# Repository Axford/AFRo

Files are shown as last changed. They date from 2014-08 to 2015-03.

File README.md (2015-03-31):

# AFRo

Assisted Feeding Robot

In development for REMAP UK

Design notes (WIP):
https://docs.google.com/document/d/1HDJsVby1FxGu6IQ2XBOvq7dboFC9hibPxshcKR86C0M/pub

## Hardware

OpenSCAD model, assembly guide and STL for printed parts

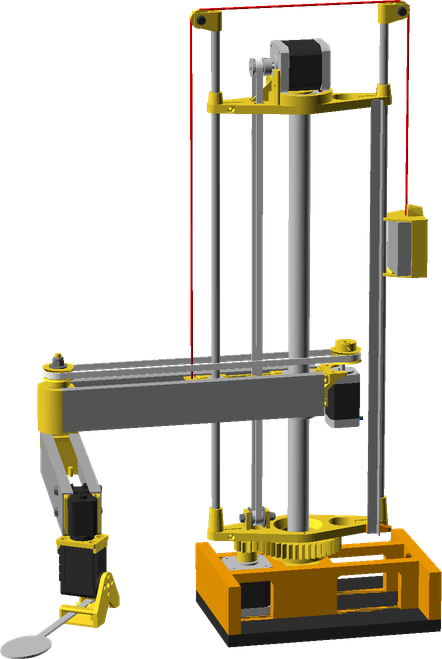
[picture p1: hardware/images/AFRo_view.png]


## Software

**AFRoHost**
Host interface for controlling/debugging the arm, written in Processing.  

Requires the following libraries:
 - gwoptics, from http://www.gwoptics.org/processing/gwoptics_p5lib/
 - controlP5, from http://www.sojamo.de/libraries/controlP5

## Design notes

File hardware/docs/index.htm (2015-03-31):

# AFRo Documentation

## Assembly Guide

- AFRo

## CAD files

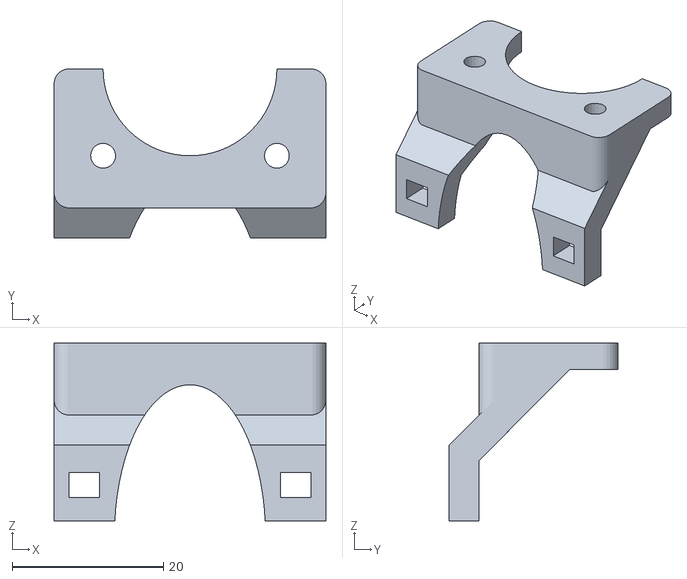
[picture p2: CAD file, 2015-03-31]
hardware/printedparts/stl/ElbowMotorPlate.stl
36.0 x 22.4 x 23.5

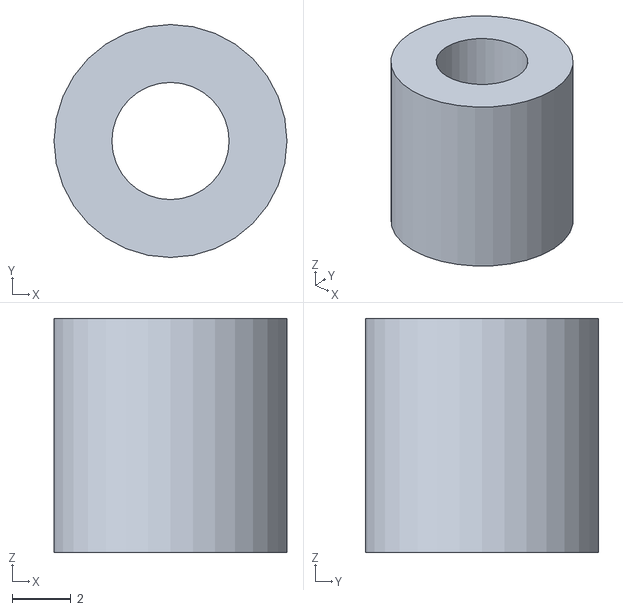
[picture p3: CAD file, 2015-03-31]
hardware/sandbox/stl/elbow bearing adapter.stl
7.95 x 7.95 x 8.00

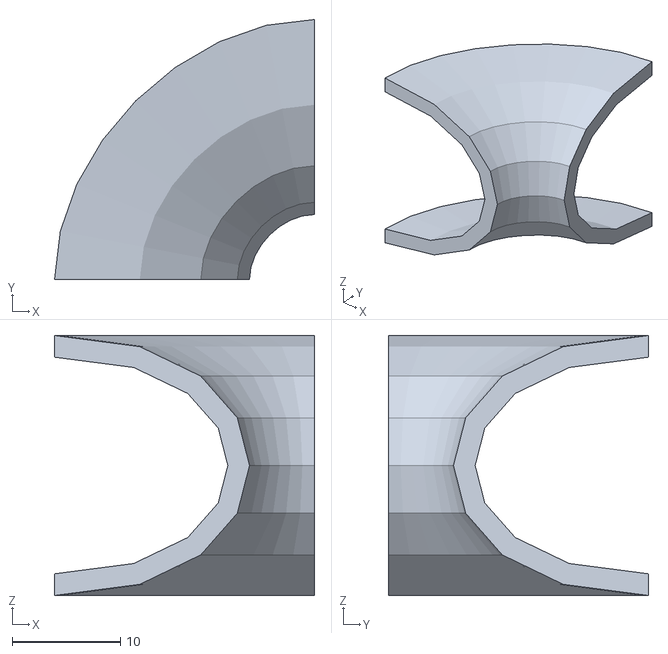
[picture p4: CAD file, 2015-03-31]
hardware/utils/surfacesolids/curve_section.stl
24.0 x 24.0 x 24.0

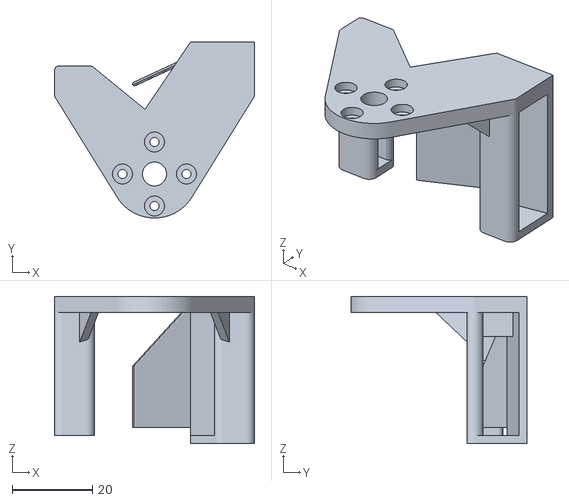
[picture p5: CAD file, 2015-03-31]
hardware/printedparts/stl/SpoonHolder.stl
50.0 x 44.0 x 36.8

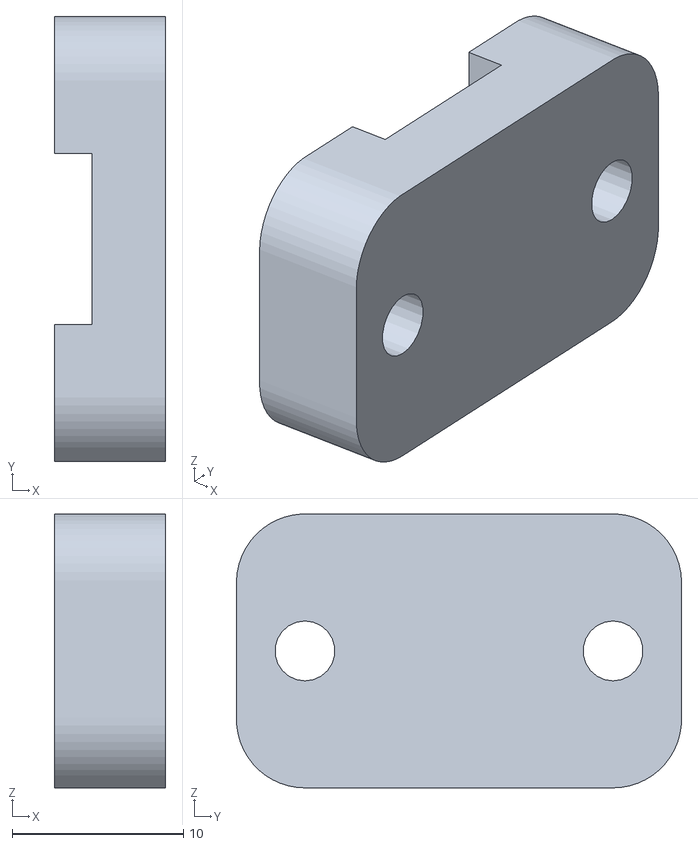
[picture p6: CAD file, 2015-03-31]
hardware/printedparts/stl/ShoulderBeltClamp.stl
6.50 x 26.0 x 16.0

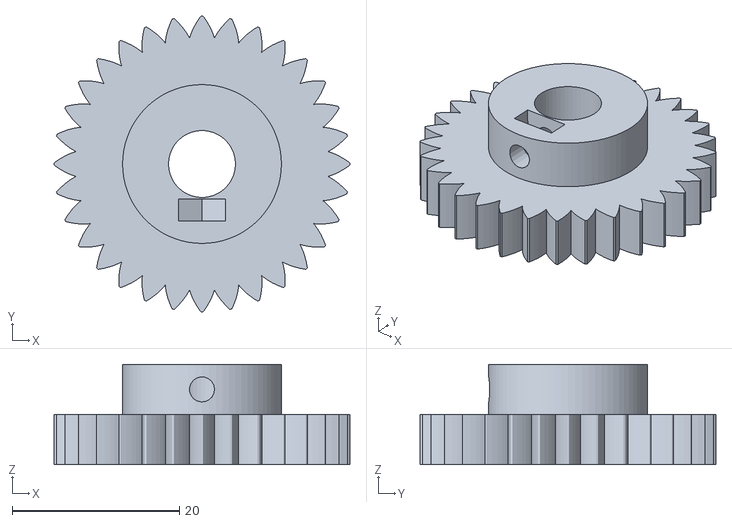
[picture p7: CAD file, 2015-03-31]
hardware/printedparts/stl/ElbowDrivenGear.stl
35.4 x 35.4 x 12.0

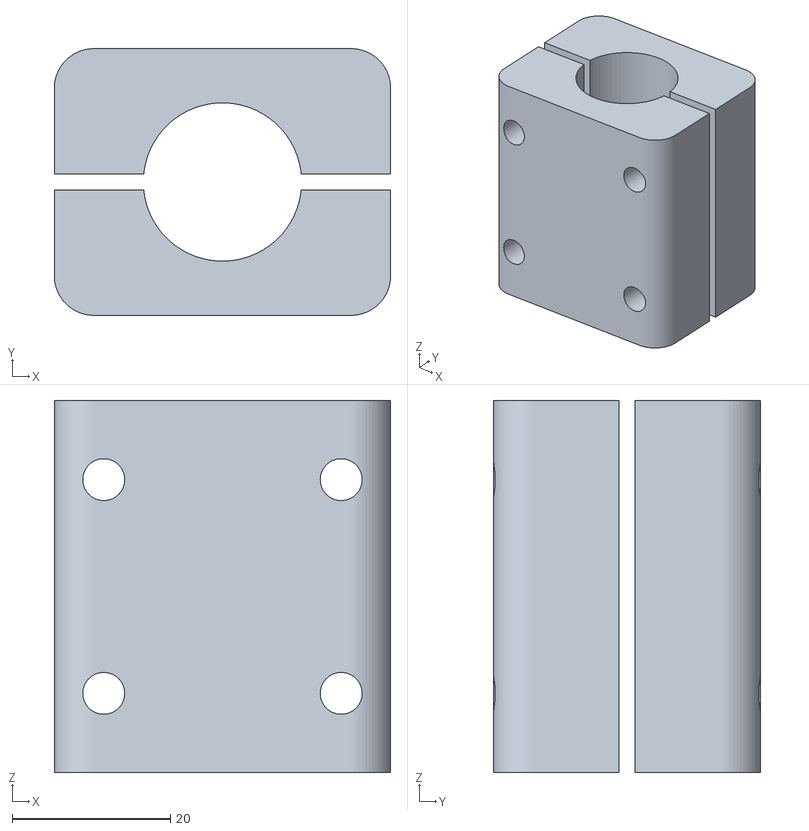
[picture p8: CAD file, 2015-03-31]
hardware/printedparts/stl/BaseBracket.stl
42.5 x 33.7 x 47.0

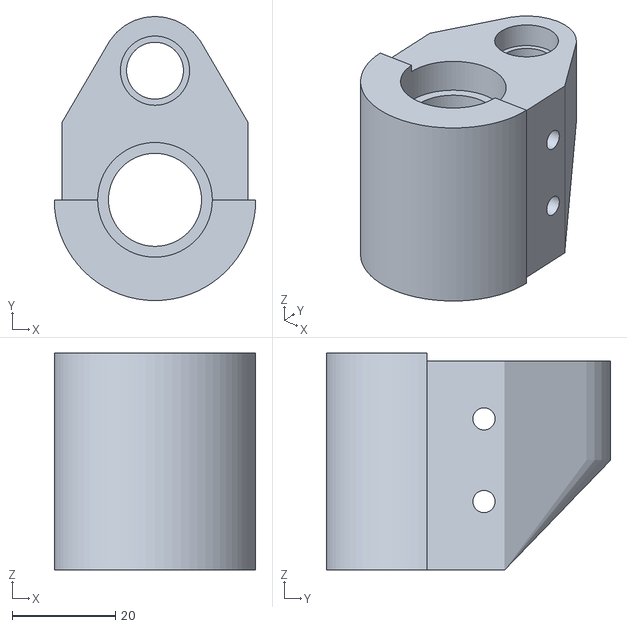
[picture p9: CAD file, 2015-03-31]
hardware/printedparts/stl/ElbowJoint.stl
39.0 x 55.0 x 42.0

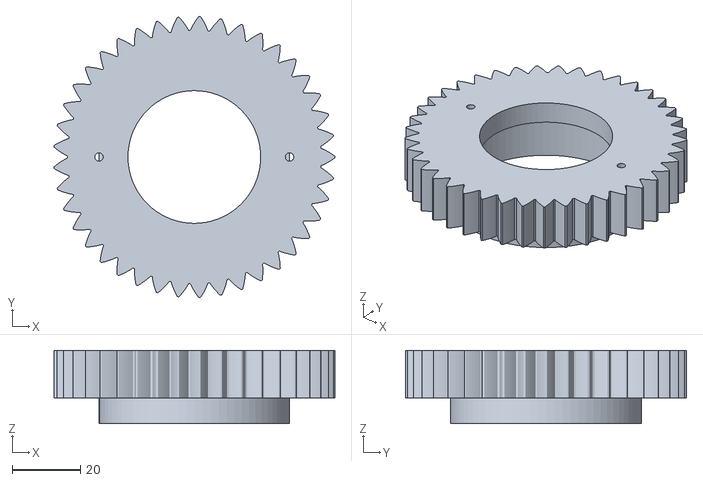
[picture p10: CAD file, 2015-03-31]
hardware/printedparts/stl/TorsoBigGear.stl
82.6 x 82.6 x 21.5

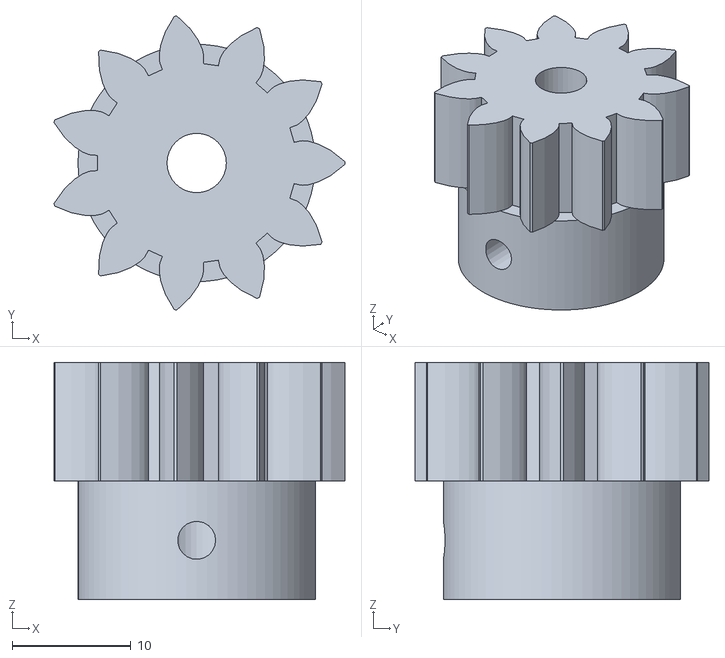
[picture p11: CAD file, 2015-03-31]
hardware/printedparts/stl/TorsoDriveGear.stl
24.5 x 24.8 x 20.0

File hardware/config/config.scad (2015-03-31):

//
// PMount
//
// Configuration file
//
bom = 0;                        // 0 no bom, 1 assemblies and stls, 2 vitamins as well
exploded = 0;                   // 1 for exploded view
simplify = false;    			// reduces complexity of some parts, e.g. alu extrusions

show_jigs = true;               // show printed jigs required to build the machine
show_support = true;            // show support structures, must be set when generating STLs

debugConnectors = false;  //  show "attach" points

// Real-world colors for various parts & vitamins
use_realistic_colors = true;    // true for "real" colors, false for "distinct" colors (useful during design and for build instructions)
printed_plastic_color = "orange";
cable_strip_real_color = "fuchsia";
belt_real_color = "yellow";
bulldog_real_color ="black";

eta = 0.01;                     // small fudge factor to stop CSG barfing on coincident faces.
$fa = 5;
$fs = 0.5;

perim = 0.5;    // perim extrusion width for 0.2 or 0.3 layer height
layers = 0.3;
2perim = 2*perim;
4perim = 4*perim;


// Debugging

DebugConnectors = 1;  			// set to 1 to debug, set to 0 for production
DebugCoordinateFrames = 1; 		// set to 1 to debug, set to 0 for production


// Visualisation

// set to true to use STL for printed parts rather than rendering on the fly
UseSTL = true;
STLPath = "../printedparts/stl/";
UseVitaminSTL = true;
VitaminSTL = "../vitamins/stl/";

$Explode  = false;
$ShowStep = 100;

$DefaultViewSize = [400, 300];


//
// Hole sizes
//
No2_pilot_radius = 1.7 / 2;       // self tapper into ABS
No4_pilot_radius = 2.0 / 2;       // wood screw into soft wood
No6_pilot_radius = 2.0 / 2;       // wood screw into soft wood

No2_clearance_radius = 2.5 / 2;
No4_clearance_radius = 3.5 / 2;
No6_clearance_radius = 4.0 / 2;

M2_tap_radius = 1.5 / 2;
M2_clearance_radius = 2.3 / 2;
M2_nut_radius = 4.6 / 2;
M2_nut_trap_depth = 2;

M2p5_tap_radius = 2.05 / 2;
M2p5_clearance_radius= 2.8 / 2;   // M2.5
M2p5_nut_trap_depth = 2.5;

M3_tap_radius = 2.5 / 2;
M3_clearance_radius = 3.3 / 2;
M3_nut_radius = 6.5 / 2;
M3_nut_trap_depth = 3;

M4_tap_radius = 3.3 / 2;
M4_clearance_radius = 2.2;
M4_nut_radius = 8.2 / 2;
M4_nut_trap_depth = 4;

M5_tap_radius = 4.2 / 2;
M5_clearance_radius = 5.3 / 2;
M5_nut_radius = 9.2 / 2;
M5_nut_depth = 4;

M6_tap_radius = 5 / 2;
M6_clearance_radius = 6.4 / 2;
M6_nut_radius = 11.6 / 2;
M6_nut_depth = 5;

M8_tap_radius = 6.75 / 2;
M8_clearance_radius = 8.4 / 2;
M8_nut_radius = 15.4 / 2;
M8_nut_depth = 6.5;

M10_tap_radius = 8 / 2;
M10_clearance_radius = 10.4 / 2;
M10_nut_radius = 19.6 / 2;
M10_nut_depth = 8;



include <colors.scad>
include <utils.scad>
include <vitamins.scad>
include <machine.scad>
include <cutparts.scad>
include <printedparts.scad>
include <assemblies.scad>

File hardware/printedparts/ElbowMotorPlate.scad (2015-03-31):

module ElbowMotorPlate_stl() {
	// origin at post, base of shoulder
	
	bh = linear_bearing_height(ShoulderRodBearing);
	bigod = linear_bearing_od(LM20UU);
	nw = NEMA_width(NEMA11);
	
	sw = ShoulderWidth;
	
	edgeOfBracket = bigod/2 + tw;
	
	d = ElbowMotorOffset;

	d1 = d - edgeOfBracket -  tw;
	
	printedPart("printedparts/ElbowMotorPlate.scad", "Elbow Motor Plate", "ElbowMotorPlate_stl()") {

        view(t=[-1, 2, 3]);

        if (UseSTL) {
            import(str(STLPath, "ElbowMotorPlate.stl"));
        } else {
            difference() {
                union() {

                    // motor plate
                    translate([-sw/2, edgeOfBracket + tw, bh -dw ])
                        roundedRect([sw, d1, dw + 1.5], tw/2);

                    // back rest
                    translate([-sw/2, edgeOfBracket + tw, dw ])
                        roundedRect([sw, tw, bh - dw], tw/2);

                    // mating plate
                    translate([-sw/2, edgeOfBracket + eta, 14 - dw ])
                        rotate([0, 90, 0])
                        trapezoidPrism(14 + tw/2, 14-tw, tw + tw/2, -tw - tw/2, sw);

                    // fillets
                    for (i=[0,1])
                        mirror([i,0,0])
                        translate([sw/2 - dw/2, edgeOfBracket + tw + tw/2, bh - dw])
                        rotate([0, 90, 0])
                        right_triangle(10, 10, dw, center = true);

                    // back rest fillet

                }

                // motor fixings / boss
                translate([0, ElbowMotorOffset, bh+1.5]) {
                    // boss
                    cylinder(r=NEMA_big_hole(NEMA11)+0.3, h=50, center=true);

                    // motor fixings
                    for(a = [0: 90 : 90 * (4 - 1)])
                        rotate([0, 0, a])
                        translate([NEMA_holes(NEMA11)[0], NEMA_holes(NEMA11)[1], 0])
                        cylinder(r=screw_clearance_radius(M3_cap_screw), h=50, center=true);
                }

                // shoulder bracket fixings
                for (i=[0,1])
                    mirror([i,0,0])
                    translate([ShoulderWidth/2 - tw, edgeOfBracket, bh - ShoulderHeight/2 + 2]) {
                        // bore
                        cube([4, 100, 3.3], center=true);

                    }

                // trim for screw heads
                translate([-sw/2-5, edgeOfBracket + tw, 12 - dw - eta ])
                    rotate([0, 90, 0])
                    trapezoidPrism(12 + tw/2, 12-tw, tw + tw/2, -tw - tw/2, sw+10);

                // weight loss
                translate([0,0, 0])
                    scale([0.5,1,1])
                    rotate([90,0, 0])
                    cylinder(r=20, h=100, center=true);

            }
        }
    }
}

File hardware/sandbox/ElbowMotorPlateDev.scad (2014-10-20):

include <../config/config.scad>


ShoulderBracketLeft_stl();
ShoulderBracketRight_stl();

ElbowMotorPlate_stl();

bh = linear_bearing_height(ShoulderRodBearing);

// motor frame
translate([0, ElbowMotorOffset, bh - dw])
	frame();


translate([-80, 0, 0]) ShoulderAssembly();

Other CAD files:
hardware/sandbox/printedpart_ElbowMotorPlate.scad
assemblies/LowerArm.scad
assemblies/UpperArm.scad
hardware/AFRo.scad
hardware/assemblies/AFRo.scad
hardware/assemblies/CableGuide.scad
hardware/assemblies/Hand.scad
hardware/assemblies/LowerArm.scad
hardware/assemblies/Shoulder.scad
hardware/assemblies/Torso.scad
hardware/assemblies/mk1/AFRo.scad
hardware/assemblies/mk1/Hand.scad
hardware/assemblies/mk1/LowerArm.scad
hardware/assemblies/mk1/MotorCoupling.scad
hardware/assemblies/mk1/Shoulder.scad
hardware/assemblies/mk1/UpperArm.scad
hardware/config/assemblies.scad
hardware/config/colors.scad
hardware/config/cutparts.scad
hardware/config/machine.scad
hardware/config/machine_mk1.scad
hardware/config/printedparts.scad
hardware/config/utils.scad
hardware/config/vitamins.scad
hardware/cutparts/LowerArmLeftSide.scad
hardware/design/scara concept 1.skp
hardware/design/scara concept 1~.skp
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

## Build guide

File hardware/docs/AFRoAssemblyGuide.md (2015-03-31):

# AFRo
# Assembly Guide

## Bill of Materials

Make sure you have all of the following parts before you begin.

### Vitamins

Qty | Vitamin | Image
--- | --- | ---
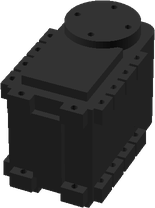
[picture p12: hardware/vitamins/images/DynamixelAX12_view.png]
2 | [Dynamixel AX12]() |  | 
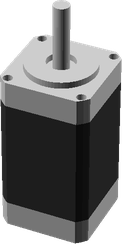
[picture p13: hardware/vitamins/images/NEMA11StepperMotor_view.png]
1 | [NEMA11 Stepper Motor]() |  | 
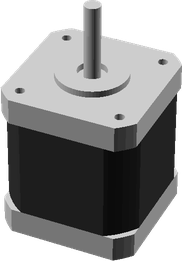
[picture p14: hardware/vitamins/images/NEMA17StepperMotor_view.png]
2 | [NEMA17 Stepper Motor]() |  | 
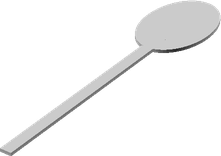
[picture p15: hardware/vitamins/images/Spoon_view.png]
1 | [Spoon]() |  | 
1 | [Threaded Rod M6 x 105mm]() |  | 
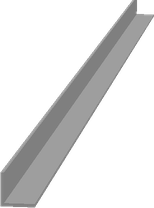
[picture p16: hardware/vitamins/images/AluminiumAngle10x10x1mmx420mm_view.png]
1 | [Aluminium Angle 10x10x1mm x 420mm]() |  | 
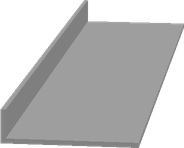
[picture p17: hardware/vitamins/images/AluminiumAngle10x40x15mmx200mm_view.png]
4 | [Aluminium Angle 10x40x1.5mm x 200mm]() |  | 
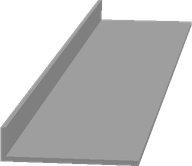
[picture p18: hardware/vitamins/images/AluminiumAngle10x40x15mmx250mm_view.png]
2 | [Aluminium Angle 10x40x1.5mm x 250mm]() |  | 
1 | [Aluminium Tube 8mm OD 6mm ID x 79mm]() |  | 
2 | [Ball Bearing 608]() |  | 
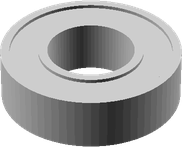
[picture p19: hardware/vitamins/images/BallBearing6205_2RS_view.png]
2 | [Ball Bearing 6205_2RS]() |  | 
6 | [Ball Bearing 624]() |  | 
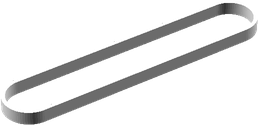
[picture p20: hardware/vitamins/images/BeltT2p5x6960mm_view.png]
1 | [Belt T2p5x6 960mm]() |  | 
1 | [Belt T2p5x6 610mm]() |  | 
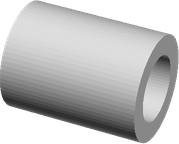
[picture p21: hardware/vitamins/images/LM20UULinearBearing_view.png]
1 | [LM20UU Linear Bearing]() |  | 
1 | [LM8UU Linear Bearing]() |  | 
1 | [T2.5x18 Pulley]() |  | 
4 | [M2 Nut]() |  | 
6 | [Nyloc M4 Nut]() |  | 
1 | [M6 Nut]() |  | 
1 | [Nyloc M6 Nut]() |  | 
12 | [M2 pan screw x 6mm]() |  | 
2 | [M4 cap screw x 20mm]() |  | 
1 | [M4 cap screw x 50mm]() |  | 
1 | [M4 hex screw x 30mm]() |  | 
2 | [M4 hex screw x 40mm]() |  | 
19 | [M4 Washer 9x0.8]() |  | 
2 | [M5 Washer 20x1.4]() |  | 
4 | [M6 Washer 12x1.5]() |  | 
1 | [M8 Washer 17x1.8]() |  | 

### Cut Parts

Qty | Part Name | Image
--- | --- | ---
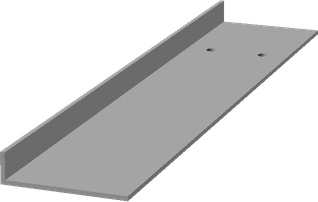
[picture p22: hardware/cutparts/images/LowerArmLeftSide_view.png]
2 | Lower Arm Left Side |  | 

### Printed Parts

Qty | Part Name | Image
--- | --- | ---
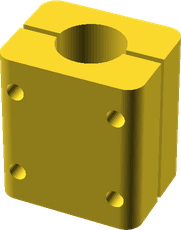
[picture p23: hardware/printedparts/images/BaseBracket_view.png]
1 | [Base Bracket](../printedparts/stl/BaseBracket.stl) |  | 
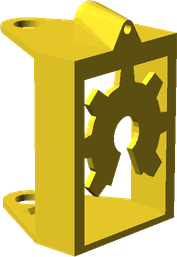
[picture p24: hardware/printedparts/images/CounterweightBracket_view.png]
1 | [Counterweight Bracket](../printedparts/stl/CounterweightBracket.stl) |  | 
2 | [Counterweight Idler Guide](../printedparts/stl/CounterweightIdlerGuide.stl) |  | 
2 | [Counterweight Idler](../printedparts/stl/CounterweightIdler.stl) |  | 
1 | [Counterweight Line Bracket](../printedparts/stl/CounterweightLineBracket.stl) |  | 
1 | [Elbow Drive Pulley](../printedparts/stl/ElbowDrivePulley.stl) |  | 
1 | [Elbow Driven Gear](../printedparts/stl/ElbowDrivenGear.stl) |  | 
1 | [Elbow Driven Pulley](../printedparts/stl/ElbowDrivenPulley.stl) |  | 
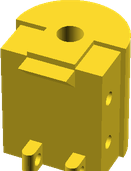
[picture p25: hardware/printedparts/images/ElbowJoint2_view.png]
1 | [Elbow Joint 2](../printedparts/stl/ElbowJoint2.stl) |  | 
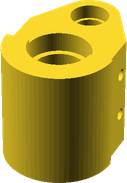
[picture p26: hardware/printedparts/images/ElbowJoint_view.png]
1 | [Elbow Joint](../printedparts/stl/ElbowJoint.stl) |  | 
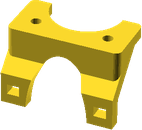
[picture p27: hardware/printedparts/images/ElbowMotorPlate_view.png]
1 | [Elbow Motor Plate](../printedparts/stl/ElbowMotorPlate.stl) |  | 
2 | [Lower Arm Servo Bracket](../printedparts/stl/LowerArmServoBracket.stl) |  | 
1 | [Shoulder Belt Clamp](../printedparts/stl/ShoulderBeltClamp.stl) |  | 
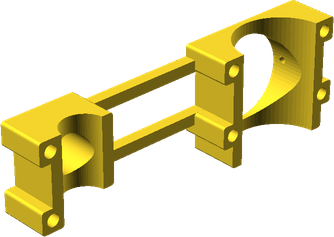
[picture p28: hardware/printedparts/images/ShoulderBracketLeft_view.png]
1 | [Shoulder Bracket Left](../printedparts/stl/ShoulderBracketLeft.stl) |  | 
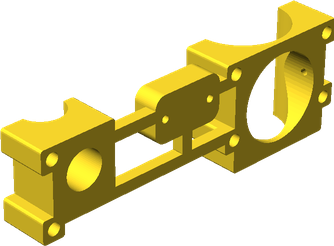
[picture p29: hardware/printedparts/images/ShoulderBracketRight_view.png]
1 | [Shoulder Bracket Right](../printedparts/stl/ShoulderBracketRight.stl) |  | 
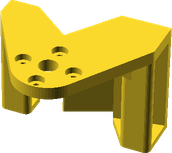
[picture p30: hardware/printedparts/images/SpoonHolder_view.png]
1 | [Spoon Holder](../printedparts/stl/SpoonHolder.stl) |  | 
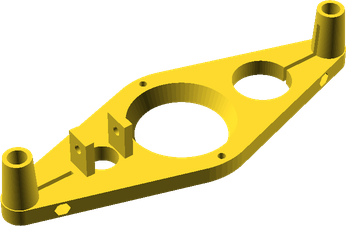
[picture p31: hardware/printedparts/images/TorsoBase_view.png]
1 | [Torso Base](../printedparts/stl/TorsoBase.stl) |  | 
1 | [Torso Bearing Collar](../printedparts/stl/TorsoBearingCollar.stl) |  | 
1 | [Torso Bearing Top Collar](../printedparts/stl/TorsoBearingTopCollar.stl) |  | 
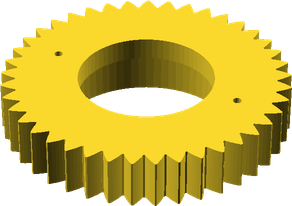
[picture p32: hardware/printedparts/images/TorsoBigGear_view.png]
1 | [Torso Big Gear](../printedparts/stl/TorsoBigGear.stl) |  | 
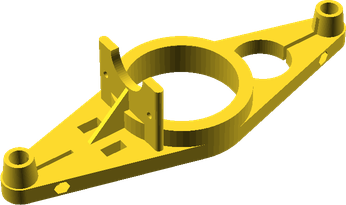
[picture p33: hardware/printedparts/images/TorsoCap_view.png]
1 | [Torso Cap](../printedparts/stl/TorsoCap.stl) |  | 
1 | [Torso Drive Gear](../printedparts/stl/TorsoDriveGear.stl) |  | 
1 | [Wrist Bracket](../printedparts/stl/WristBracket.stl) |  | 

# Cutting Instructions

## Lower Arm Left Side (x2)

### Vitamins

Qty | Vitamin | Image
--- | --- | ---
4 | [Aluminium Angle 10x40x1.5mm x 200mm]() |  | 

### Fabrication Steps

1. Cut aluminium angle to 200mm
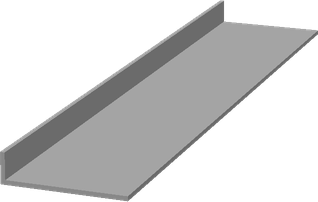
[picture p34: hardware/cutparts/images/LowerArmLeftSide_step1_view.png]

2. Drill 4mm diameter fixing holes


# Assembly Instructions

## Spoon

### Vitamins

Qty | Vitamin | Image
--- | --- | ---
1 | [Dynamixel AX12]() |  | 
1 | [Spoon]() |  | 
4 | [M2 Nut]() |  | 
4 | [M2 pan screw x 6mm]() |  | 

### Printed Parts

Qty | Part Name | Image
--- | --- | ---
1 | [Spoon Holder](../printedparts/stl/SpoonHolder.stl) |  | 

### Assembly Steps

1. Push M2 nuts into the back of the servo fixing tabs
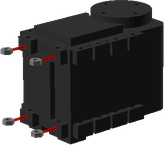
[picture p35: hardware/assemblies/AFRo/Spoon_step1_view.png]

2. Attach the spoon holder to the servo
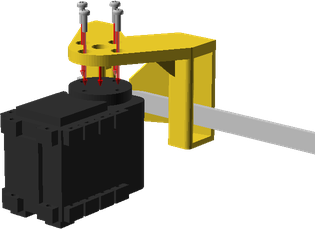
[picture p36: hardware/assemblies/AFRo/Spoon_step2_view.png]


## Hand

### Vitamins

Qty | Vitamin | Image
--- | --- | ---
1 | [Dynamixel AX12]() |  | 
8 | [M2 pan screw x 6mm]() |  | 

### Printed Parts

Qty | Part Name | Image
--- | --- | ---
1 | [Wrist Bracket](../printedparts/stl/WristBracket.stl) |  | 

### Sub-Assemblies

Qty | Name 
--- | --- 
1 | Spoon

### Assembly Steps

1. Screw the wrist bracket onto the wrist servo
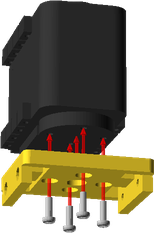
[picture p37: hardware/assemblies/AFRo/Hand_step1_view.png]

2. Push the spoon assembly into the wrist bracket
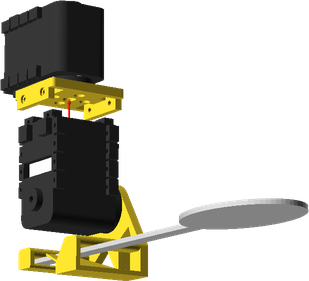
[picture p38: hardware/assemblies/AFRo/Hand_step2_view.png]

3. Screw through the bracket into the servo fixings
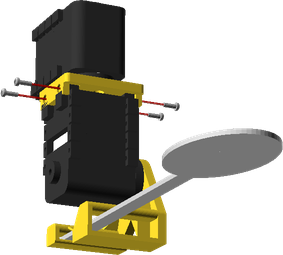
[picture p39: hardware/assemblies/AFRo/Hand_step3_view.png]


## Lower Arm

### Vitamins

Qty | Vitamin | Image
--- | --- | ---
2 | [Nyloc M4 Nut]() |  | 
2 | [M4 hex screw x 40mm]() |  | 
4 | [M4 Washer 9x0.8]() |  | 

### Printed Parts

Qty | Part Name | Image
--- | --- | ---
1 | [Elbow Joint 2](../printedparts/stl/ElbowJoint2.stl) |  | 
2 | [Lower Arm Servo Bracket](../printedparts/stl/LowerArmServoBracket.stl) |  | 

### Sub-Assemblies

Qty | Name 
--- | --- 
1 | Hand

### Assembly Steps

1. Push the servo brackets onto the servo, optionally screw them into place
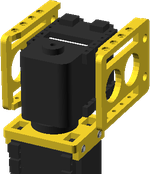
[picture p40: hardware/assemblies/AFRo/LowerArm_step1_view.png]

2. Bolt through the aluminium channels and servo brackets
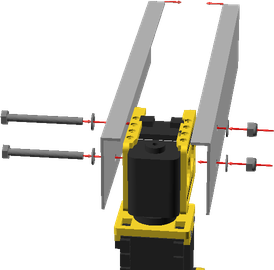
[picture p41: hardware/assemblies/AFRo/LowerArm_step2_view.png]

3. Bolt through the aluminium channels and elbow joint
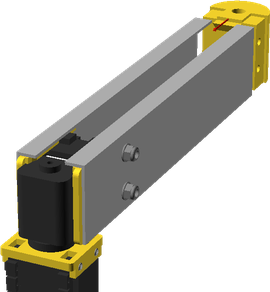
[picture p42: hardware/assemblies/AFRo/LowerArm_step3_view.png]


## Elbow Joint

### Vitamins

Qty | Vitamin | Image
--- | --- | ---
1 | [Threaded Rod M6 x 105mm]() |  | 
1 | [Aluminium Tube 8mm OD 6mm ID x 79mm]() |  | 
2 | [Ball Bearing 608]() |  | 
2 | [Ball Bearing 624]() |  | 
1 | [Belt T2p5x6 610mm]() |  | 
1 | [Nyloc M4 Nut]() |  | 
1 | [M6 Nut]() |  | 
1 | [Nyloc M6 Nut]() |  | 
1 | [M4 cap screw x 50mm]() |  | 
3 | [M4 Washer 9x0.8]() |  | 
4 | [M6 Washer 12x1.5]() |  | 
1 | [M8 Washer 17x1.8]() |  | 

### Printed Parts

Qty | Part Name | Image
--- | --- | ---
1 | [Elbow Driven Gear](../printedparts/stl/ElbowDrivenGear.stl) |  | 
1 | [Elbow Driven Pulley](../printedparts/stl/ElbowDrivenPulley.stl) |  | 
1 | [Elbow Joint](../printedparts/stl/ElbowJoint.stl) |  | 

### Sub-Assemblies

Qty | Name 
--- | --- 
1 | Lower Arm

### Assembly Steps

1. Loosely assemble the driven gear set and push fit into the elbow joint
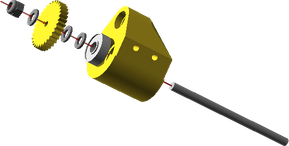
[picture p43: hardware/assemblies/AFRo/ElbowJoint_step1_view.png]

2. Assemble the pulley set
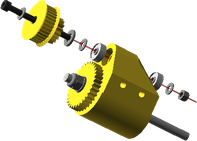
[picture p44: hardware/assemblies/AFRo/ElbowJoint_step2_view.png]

3. Slide the aluminium tube over the threaded rod and push fit the lower bearing
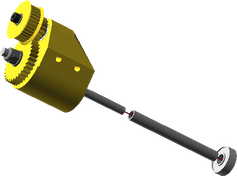
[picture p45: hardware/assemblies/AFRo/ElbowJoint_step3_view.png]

4. Connect the lower arm
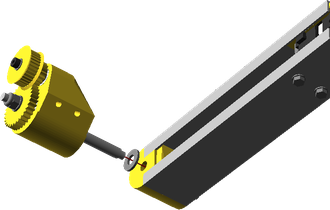
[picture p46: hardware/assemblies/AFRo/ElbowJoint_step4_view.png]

5. Slip the belt round the pulley - this be connected later
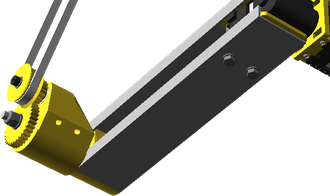
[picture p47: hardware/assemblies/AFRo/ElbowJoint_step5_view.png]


## Counterweight Idler (x2)

### Vitamins

Qty | Vitamin | Image
--- | --- | ---
2 | [Ball Bearing 624]() |  | 
2 | [Nyloc M4 Nut]() |  | 
2 | [M4 cap screw x 20mm]() |  | 
8 | [M4 Washer 9x0.8]() |  | 

### Printed Parts

Qty | Part Name | Image
--- | --- | ---
2 | [Counterweight Idler Guide](../printedparts/stl/CounterweightIdlerGuide.stl) |  | 
2 | [Counterweight Idler](../printedparts/stl/CounterweightIdler.stl) |  | 

## Shoulder

### Vitamins

Qty | Vitamin | Image
--- | --- | ---
1 | [NEMA11 Stepper Motor]() |  | 
2 | [Aluminium Angle 10x40x1.5mm x 250mm]() |  | 
1 | [LM20UU Linear Bearing]() |  | 
1 | [LM8UU Linear Bearing]() |  | 

### Printed Parts

Qty | Part Name | Image
--- | --- | ---
1 | [Counterweight Line Bracket](../printedparts/stl/CounterweightLineBracket.stl) |  | 
1 | [Elbow Drive Pulley](../printedparts/stl/ElbowDrivePulley.stl) |  | 
1 | [Elbow Motor Plate](../printedparts/stl/ElbowMotorPlate.stl) |  | 
1 | [Shoulder Belt Clamp](../printedparts/stl/ShoulderBeltClamp.stl) |  | 
1 | [Shoulder Bracket Left](../printedparts/stl/ShoulderBracketLeft.stl) |  | 
1 | [Shoulder Bracket Right](../printedparts/stl/ShoulderBracketRight.stl) |  | 

### Sub-Assemblies

Qty | Name 
--- | --- 
1 | Elbow Joint

## Counterweight

### Printed Parts

Qty | Part Name | Image
--- | --- | ---
1 | [Counterweight Bracket](../printedparts/stl/CounterweightBracket.stl) |  | 

## Cable Guide

### Vitamins

Qty | Vitamin | Image
--- | --- | ---
1 | [Aluminium Angle 10x10x1mm x 420mm]() |  | 

## Torso

### Vitamins

Qty | Vitamin | Image
--- | --- | ---
1 | [NEMA17 Stepper Motor]() |  | 
2 | [Ball Bearing 6205_2RS]() |  | 
2 | [Ball Bearing 624]() |  | 
1 | [Belt T2p5x6 960mm]() |  | 
1 | [T2.5x18 Pulley]() |  | 
1 | [Nyloc M4 Nut]() |  | 
1 | [M4 hex screw x 30mm]() |  | 
4 | [M4 Washer 9x0.8]() |  | 
2 | [M5 Washer 20x1.4]() |  | 

### Printed Parts

Qty | Part Name | Image
--- | --- | ---
1 | [Torso Base](../printedparts/stl/TorsoBase.stl) |  | 
1 | [Torso Bearing Collar](../printedparts/stl/TorsoBearingCollar.stl) |  | 
1 | [Torso Bearing Top Collar](../printedparts/stl/TorsoBearingTopCollar.stl) |  | 
1 | [Torso Big Gear](../printedparts/stl/TorsoBigGear.stl) |  | 
1 | [Torso Cap](../printedparts/stl/TorsoCap.stl) |  | 

### Sub-Assemblies

Qty | Name 
--- | --- 
2 | Counterweight Idler
1 | Shoulder
1 | Counterweight
1 | Cable Guide

## Torso Drive

### Vitamins

Qty | Vitamin | Image
--- | --- | ---
1 | [NEMA17 Stepper Motor]() |  | 

### Printed Parts

Qty | Part Name | Image
--- | --- | ---
1 | [Torso Drive Gear](../printedparts/stl/TorsoDriveGear.stl) |  | 

## AFRo

### Printed Parts

Qty | Part Name | Image
--- | --- | ---
1 | [Base Bracket](../printedparts/stl/BaseBracket.stl) |  | 

### Sub-Assemblies

Qty | Name 
--- | --- 
1 | Torso
1 | Torso Drive

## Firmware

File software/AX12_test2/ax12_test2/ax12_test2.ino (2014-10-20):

#include <ax12.h>

// using X driver on RAMPS 1.4....

/*
#define Z_STEP_PIN         A0
#define Z_DIR_PIN          A1
#define Z_ENABLE_PIN       38
*/

/*
// E0
#define Z_STEP_PIN         26
#define Z_DIR_PIN          28
#define Z_ENABLE_PIN       24

*/

// E1 on RAMPS 1.4
#define Z_STEP_PIN         36
#define Z_DIR_PIN          34
#define Z_ENABLE_PIN       30

// SAM-3 Servo interface



AX12 motor1;
AX12 motor2;
AX12 motor3;

int spoonTorq = 2;
int spoonID = 0;

void enable_z() {
   //WRITE(Z_ENABLE_PIN, LOW);
   digitalWrite(Z_ENABLE_PIN, LOW);
}

void disable_z() {
   //WRITE(Z_ENABLE_PIN, HIGH); 
   digitalWrite(Z_ENABLE_PIN, HIGH);
}

void setup() {
 
  motor1 = AX12();
  motor2 = AX12();
  motor3 = AX12();

  Serial.begin (115200);  // inicializa el Serial a 115,2 Kb/s
  AX12::init (1000000);   // inicializa los AX12 a 1 Mb/s

  motor1.id = 3; 
  motor1.SRL = RETURN_READ;
 
  motor2.id = 2;  
  motor2.SRL = RETURN_ALL;
  
  motor3.id = 1;  
  motor3.SRL = RETURN_ALL;
  
  pinMode(Z_ENABLE_PIN, OUTPUT);
  pinMode(Z_STEP_PIN, OUTPUT);  
  pinMode(Z_DIR_PIN, OUTPUT);
  
  pinMode(13, OUTPUT);

  enable_z();    
  //disable_z();
  
  noInterrupts();
  
  // set up Timer 1
  TCCR1A = 0;          // normal operation
  TCCR1B = bit(WGM12) | bit(CS11);   // CTC, scale / 8
  //OCR1A =  625;       // compare A register value, approx 1 RPM with 200 steps per rev and 16x microstepping
  // ORC1A =     // 1 RPM with 200 steps per rev and 2x microstepping
  OCR1A = 500;
  TIMSK1 = bit (OCIE1A);             // interrupt on Compare A Match
  
  // set up Timer 3
  TCCR3A = 0;          // normal operation
  TCCR3B = bit(WGM12) | bit(CS12) | bit(CS10);   // CTC, scale / 1024
  OCR3A =  156;       // compare A register value, approx 100 Hz
  TIMSK3 = bit (OCIE3A);             // interrupt on Compare A Match
  
  // set default velocities
  motor1.setVel(200);
  motor2.setVel(200);
  motor3.setVel(200);
  
  // set initial torques
  motor1.setTorque(500);
  motor2.setTorque(400);
  motor3.setTorque(200);
  
  // set initial positions
  motor1.setPos(512);
  motor2.setPos(512);
  motor3.setPos(512);
  
  // punch
  motor1.writeInfo(PUNCH, 60);
  motor2.writeInfo(PUNCH, 50);
  
  // compliance margins
  motor1.writeInfo(CW_COMPLIANCE_MARGIN, 0);
  motor1.writeInfo(CCW_COMPLIANCE_MARGIN, 0);
 
  // compliance slopes
  motor1.writeInfo(CW_COMPLIANCE_SLOPE, 64);
  motor1.writeInfo(CCW_COMPLIANCE_SLOPE, 64);
  
  // compliance margins
  motor2.writeInfo(CW_COMPLIANCE_MARGIN, 0);
  motor2.writeInfo(CCW_COMPLIANCE_MARGIN, 0);
 
  // compliance slopes
  motor2.writeInfo(CW_COMPLIANCE_SLOPE, 32);
  motor2.writeInfo(CCW_COMPLIANCE_SLOPE, 32);
  
  // compliance margins
  motor3.writeInfo(CW_COMPLIANCE_MARGIN, 0);
  motor3.writeInfo(CCW_COMPLIANCE_MARGIN, 0);
 
  // compliance slopes
  motor3.writeInfo(CW_COMPLIANCE_SLOPE, 16);
  motor3.writeInfo(CCW_COMPLIANCE_SLOPE, 16);

  
  
  
  Serial3.begin(115200);
  
  // spoon - set speed
   int tmp1 = 0xE0 | 0;
   int tmp2 = 0x0D;
   int tmp3 = 1;
   int tmp4 = 20;
   int checksum = (tmp1 ^ tmp2 ^ tmp3 ^ tmp4) & 0x7f;
   Serial3.write(0xff);
   Serial3.write(tmp1);
   Serial3.write(tmp2);
   Serial3.write(tmp3);
   Serial3.write(tmp4);
   Serial3.write(checksum);
  
  Serial.begin(115200);
  
  delay(1000); // give them time to get there
  
  // enable interrupts
  interrupts();
}

long stepCount = 0;
long stepTimer = 500;


void step_z() {
   
   if (stepCount % 30 == 0 && stepTimer > 120) {
      stepTimer--;
      //OCR1A = stepTimer; 
   }
  
   if (stepCount < (long)3200 * 15) {
  
     digitalWrite(Z_STEP_PIN, true);
     digitalWrite(Z_STEP_PIN, false);
   
   }
   
   stepCount++;
   
   if (stepCount > (long)3200 * 16) {
      digitalWrite(Z_DIR_PIN, !digitalRead(Z_DIR_PIN)); 
      stepCount = 0;
      stepTimer = 500;
   }
}

int vel = 1;
int maxVel = 200;
int i = 0;


volatile boolean moveDone = true;
int startPos = 512;
int endPos = 512;
int posChange = 0;
int eventCount = 10 * 2;
int events = 0;


ISR(TIMER1_COMPA_vect)
{
  step_z();
}



float v0 = 10;  // jerk velocity
float v2 = 0;
float v3 = v0;
float t1, t2, t3, t4;
float d1,d2;
float tplateau;
float up, plateau, down;
float distance, vmax, a;
int accelerateUntil, decelerateAfter;

void printStrFloat(char *s, float v) {
  Serial.print(s);
  Serial.print(":");
  Serial.println(v);
}

float intersectionDistance(float s1, float s2, float a, float d) {
  return (2*a*d - s1*s1 + s2*s2) / (4*a);
}

void prepTrapezoid() {
  // assumes t0=0
  t1 = (vmax-v0) / a;  // time from v0 to vmax (time to reach full speed)
  t4 = (vmax-v3) / a; // time from vmax to v3 (time to brake)
  d1 = v0*t1 + 0.5*a*t1*t1;  // distance t0-t1
  d2 = v3*t4 + 0.5*a*t4*t4;  // distance t2-t3
  
  printStrFloat("d1",d1);
  printStrFloat("d2",d2);
  

  if( d1+d2 < distance ) {
    // plateau at vmax in the middle
    tplateau = ( distance - d1 - d2 ) / vmax; // duration of plateau
    t2 = t1 + tplateau;
    t3 = t2 + t4;
  } else {
    // start breaking before reaching vmax
    Serial.println("no coasting");
    
    float id = intersectionDistance(v0,v3,a,distance);
    printStrFloat("id",id);
   
    t1 = sqrt(2*abs(id)/a);
    t2 = t1;
    t3 = t2 + sqrt(2*abs(distance-id)/a);
    /*
    t1 = ( sqrt( 2.0*a*d2 + v0*v0 ) - v0 ) / a;
    t2 = t1;
    t3 = t2 + ( sqrt( 2.0*a*(distance-d2) + v3*v3 ) - v3 ) / a;
   */
  }
  
  accelerateUntil = round(t1 * 10);
  decelerateAfter = round(t2 * 10);
}

int getTrapezoidPos(float t) {
  if(t<t1) {
    return round(v0*t + 0.5*a*t*t);
  } 
  else if(t<t2) {
    up = v0*t1 + 0.5*a*t1*t1;
    plateau = vmax*(t-t1);
    return round(up + plateau);
  } 
  else if(t<=t3) {
    up = v0*t1 + 0.5*a*t1*t1;  // how far we've gone whilst accelerating
    plateau = vmax*(t2-t1);   // distance travelled in plateau
    t4=t-t2;  // time into decel period
    float v2 = a * t1; // velocity at end of accel period, might be vmax
    down = v2*t4 - 0.5*a*t4*t4;  // distance travelled in decel
    return round(up + plateau + down);
  } 
}

int getTrapezoidVel(float t) {
  if(t<t1) {
    return round(v0 + 0.5*a*t);
  }
  else if(t<t2) {
    return round(vmax);
  }
  else if(t<=t3) {
    t4=t-t2;
    float v2 = a * t1;
    return round(v2 - 0.5*a*t4);
  } 
}

ISR(TIMER3_COMPA_vect)
{
 interrupts();

 int p = 512;
 
 p = p + round(300 * sin(events * 0.007));
 
 
 motor1.setPos(p);
 motor2.setPos(p);
 motor3.setPos(p);
 
 events++;
  
  if (!moveDone) {
    events++;
    float t = events/10.0;
    if (t > t3 ) t = t3;
    int pos =  getTrapezoidPos(t);
    if (posChange > 0) {
       pos += startPos; 
    } else {
       pos = startPos - pos;
    }
    int vel = abs(getTrapezoidVel(t + 1/10.0));
    
    /*
    Serial.print(t);
    Serial.print(": ");
    Serial.print(pos);
    Serial.print(", ");
    Serial.println(vel);
    */
    
    motor1.setPosVel(pos,vel);
    
    if (t >= t3) {
       moveDone = true; 
    }
  }
}

void loop() {
  
  
   //delay(100);
  
  
   //motor1.setTorque(200);
   //motor2.setTorque(200);
  
   
   // shoulder
   //motor1.setPosVel(random(400, 600), 40);
   
   // elbow
  // motor2.setPosVel(random(200, 800), 60);
   
   // wrist
   //motor3.setPosVel(random(10,1000), 200);
   
   // spoon - set pos
   int tmp1 = (spoonTorq << 5) | spoonID;
   int tmp2 = random(128 - 70, 128 + 10);
   //tmp2 = 128 + 85;
   int checksum = (tmp1 ^ tmp2) & 0x7f;
   Serial3.write(0xff);
   Serial3.write(tmp1);
   Serial3.write(tmp2);
   Serial3.write(checksum);
   
   
   delay(1000);
   
    
   if (moveDone  && false) {
      // setup next move
      Serial.println();
      delay(2000);
      
      
      startPos = motor1.getPos();
      while (startPos < 0 || startPos > 1024) {
          startPos = motor1.getPos();
      }
      endPos = random(10, 1000);
      posChange = endPos - startPos;
      
      Serial.print(startPos);
      Serial.print(",");
      Serial.print(endPos);
      Serial.print(",");
      Serial.println(posChange);
      
      /*
      int vel = abs(posChange) / 2;
      if (vel > 300) vel = 300;
      if ( vel < 1) vel = 1;
      motor2.setVel(vel);
      */
      
      /*
      motor2.setVel(100);
      eventCount = round(abs(posChange) * 30 / 100);    
      */
      
      distance = abs(posChange);
      vmax = 60;
      a = 10;
      
      prepTrapezoid();
      
      Serial.print("t[]:");
      Serial.print(t1);
      Serial.print(",");
      Serial.print(t2);
      Serial.print(",");
      Serial.print(t3);
      Serial.print(",");
      Serial.println(t4);
      
      Serial.print("d[]:");
      Serial.print(d1);
      Serial.print(",");
      Serial.print(d2);
      Serial.println(",");
      
      // set initial velocity
      motor1.setVel(v0);
      
      eventCount = round(t3 * 10.0);
      
      events = 0;
      
      
     
      moveDone = false; 
   }
    
}

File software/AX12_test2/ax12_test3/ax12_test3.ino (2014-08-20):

#include <ax12.h>

#define Z_STEP_PIN         A0
#define Z_DIR_PIN          A1
#define Z_ENABLE_PIN       38


void enable_z() {
   //WRITE(Z_ENABLE_PIN, LOW);
   digitalWrite(Z_ENABLE_PIN, LOW);
}

void disable_z() {
   //WRITE(Z_ENABLE_PIN, HIGH); 
}

void setup() {
 

  Serial.begin (115200);  // inicializa el Serial a 115,2 Kb/s
  ax12Init(1000000);   // inicializa los AX12 a 1 Mb/s

  pinMode(Z_ENABLE_PIN, OUTPUT);
  pinMode(Z_STEP_PIN, OUTPUT);  
  pinMode(Z_DIR_PIN, OUTPUT);
  
  pinMode(13, OUTPUT);

  enable_z();    
}

void step_z() {
   digitalWrite(Z_STEP_PIN, true);
   digitalWrite(Z_STEP_PIN, false);
}

int vel = 1;
int maxVel = 200;
int i = 0;

void loop() {
  
    //digitalWrite(13, true);

    step_z();  
   
    
    //digitalWrite(13, false);
   delay(1);    
   
   i++;

   if (i>1000) {
       i = 0;
 
       
       
       motor2.setVel(100);
       motor2.setPos(random(300,800));
       
       motor1.setVel(100);
       motor1.setPos(random(300,800));
   }   
}

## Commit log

2014-08-20 initial commit from dropbox
    [2Dshapes.scad, AFRo.scad, AluProParts.scad, BaseBracket.stl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]
2014-10-20 Lots of updates for mk2
    [!.dxf, #.dxf, +.dxf, ,.dxf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]
2014-11-04 auto build
    [!.dxf, #.dxf, +.dxf, ,.dxf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]
2014-11-04 "auto fetch and commit"
    [!.dxf, #.dxf, +.dxf, ,.dxf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]
2014-11-04 Minor tweaks
    [Hand.scad, belts.scad]
2014-11-05 Added aluAngle vitamin
    [aluAngle.scad, vitamin_AluminiumAngle10x10x1mmx420mm.scad, vitamin_AluminiumAngle10x40x15mmx200mm.scad, vitamin_AluminiumAngle10x40x15mmx250mm.scad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]
2014-11-05 added connectors to stepper-motors
    [stepper-motors.scad]
2014-11-05 Added cut part functionality
    [LowerArm.scad, LowerArmLeftSide.scad, assemblies.scad, config.scad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]
2014-11-05 fixed bug in attach with coincident axes
    [LowerArm.scad, LowerArmLeftSide.scad, attach.scad]
2014-11-05 fixed matrix equiv attach bug
    [attach.scad]
2014-11-05 Updating hand and lowerarm with connectors
    [Hand.scad, LowerArm.scad, LowerArmLeftSide.scad, LowerArmServoBracket.scad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]
2014-11-05 refining cut parts system
    [LowerArm.scad, assembly_LowerArm.scad, attach.scad, machine.scad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]
2014-11-05 fixed bug in pullies.scad
    [pullies.scad]
2014-11-06 redesigned elbow with gearing
    [ElbowDrivenGear.scad, ElbowDrivenGear.stl, ElbowDrivenPulley.scad, ElbowDrivenPulley.stl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]
2014-11-06 elbow joint assembly instructions
    [Shoulder.scad, ThreadedRod.scad, vitamin_ThreadedRodM6x105mm.scad, vitamins.scad]
2015-03-30 modified elbow to add a basic gearbox
    [ElbowDrivenGear.scad, ElbowDrivenGear.stl, ElbowDrivenPulley.scad, ElbowDrivenPulley.stl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]
